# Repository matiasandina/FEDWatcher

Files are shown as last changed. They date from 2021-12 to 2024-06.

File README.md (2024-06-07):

# FEDWatcher

FEDWatcher is sofware to connect up to 4 [FED3 feeder devices](https://github.com/KravitzLabDevices/FED3/) to one Raspberry Pi 4. 
The Raspberry Pi communicates with the FED3 devices using software serial from the BNC/headphone jack port of the Adafruit feather into the activated UART channels on the Pi.

This repository contains:

* Python code that uses standard Raspberry Pi software and Python packages. 
* The modified software serial library used on the FED3 devices. See [softwareSerial](https://github.com/matiasandina/FEDWatcher/tree/main/softwareSerial).
* Files to print the PCB we are using as a Raspberry Pi HAT for easier interface with the Raspberry Pi 4 pinout. 
* Python code for FEDWatcher GUI, which provides a way for the user to create projects and trigger FEDWatcher easily (see pic below).

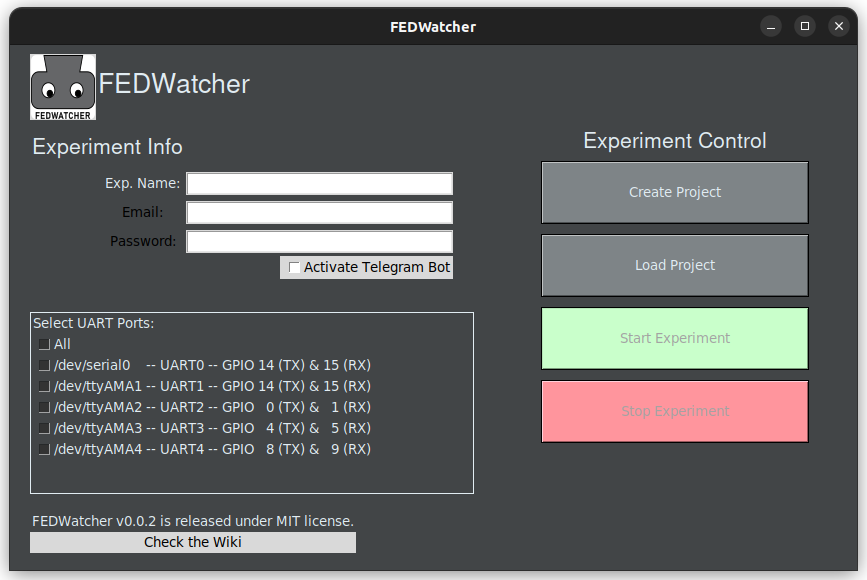
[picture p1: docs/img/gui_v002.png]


## Installation

If you already have an OS installed in your Rasberry Pi, [jump here](#edit-config). Otherwise continue reading.

To set up the Raspberry Pi, begin with flashing a standard image of Raspbian to an SD card. The project was coded and tested using Raspbian Lite with a Gnome Desktop and Raspbian Lite Buster, but any version of Raspbian should work.

For installing the operating system, the official Raspberry Pi Imager can be used. If you would like to install the Gnome desktop, the install will require that you have at least an 8GB SD card, the Pi plugged directly into a monitor, and a wifi or ethernet connection. 

### Gnome desktop

To use the Gnome desktop, first run

```
sudo raspi-config
```

Go into advanced options, select GL driver, install necessary packages if asked, and set the driver to fake KMS. Next, go back into advanced options and make sure you expand filesystem, as this is a large download. Then, back in bash, run

```
git clone https://github.com/TerraGitHuB/gnomeforpi.git && cd gnomeforpi && sudo bash gnomeforpi-install
```

This will take a long time. When the install is finished, the Raspberry Pi will reboot and you will be able to log into the Gnome desktop. In addition, the wifi will be disconnected, but you will be able to reconnect after logging in. After choosing your user and before entering your password, click the settings cog wheel under the password entry box and choose "Gnome for Xorg".

## Edit config

Next, you must enable the four hardware UARTs within the Raspberry Pi. Navigate to `/boot/` and edit `config.txt` however you prefer. This is an example using `nano`

```
sudo nano /boot/config.txt
``` 

> [!TIP]
> In newer versions, `config.txt` has been moved to `/boot/firmware/config.txt`. but everything else applies 

At the end of the file, add on the following statements:

[spi0=on]
# Settings when SPI0 is enabled: no uart4
# No need to repeat uart2, uart3, uart5 if they are always loaded

[spi0=off]
# Settings when SPI0 is disabled: include uart4
dtoverlay=uart4

[all]

dtoverlay=w1-gpio
enable_uart=1
force_eeprom_read=0
disable_poe_fan=1
dtoverlay=uart2
dtoverlay=uart3
dtoverlay=uart5

```

The first two lines disable the GPIO 0 and 1 functionality to be used for uart2. 

You can always remove/comment the first 3 lines above if you need to use a POE fan with the Pi at the same time, but it might create some unexpected erros. Please only do this if you are experienced with this type of config. 

The general mapping to. As of now, FEDWatcher only uses RX ports, but the TX pins will be reserved too.
Below there's mapping between `uartx` -> `GPIOx` -> `board pin #`

```
uart    GPIO                Board Pins (function)
--------------------------------------------------
        TXD RXD CTS RTS     
uart0   14  15              8   10
uart1   14  15              8   10
uart2   0   1   2   3       27  28  (I2C)
uart3   4   5   6   7       7   29
uart4   8   9   10  11      24  21  (SPI0)
uart5   12  13  14  15      32  33  (gpio-fan)
```

You can also check the (UART pinouts here)[https://pinout.xyz/pinout/uart].

This configuration should work when connecting FEDs directly using jumper wires or when using the HAT we designed (see further below).

> [!IMPORTANT]  
> Selecting proper pinout is key to correct functioning of the device. In general, FEDWatcher is flexible and works well with many HATs, but knowledge of the free/used pins is paramount for correct functionality.

Now, you will be able to clone the FEDWatcher github repository into your project and use the functions within it to run your own programs.

## fedwatcher python

To install the software itself, you are advised to use a virtual environment. Clone the repository and then install package requirements in the virtual environment. Installation in Raspberry Pi takes a long time, use the piwheel link in `pip3 install` to make it faster. 

Using conda:

```
git clone https://github.com/matiasandina/FEDWatcher.git
cd FEDWatcher
# tested on python 3.7.3 and 3.10
conda create -n fw_env python==3.10 pip
conda activate fw_env
pip3 install -r requirements.txt --extra-index-url https://www.piwheels.org/simple
```

Using venv (please make sure you get a python version that is compatible!): 

```
git clone https://github.com/matiasandina/FEDWatcher.git
cd FEDWatcher
python3 -m venv fedwatcher 
source fedwatcher/bin/activate
pip3 install -r requirements.txt --extra-index-url https://www.piwheels.org/simple
```

To launch the GUI.

```
cd FEDWatcher/
source fedwatcher/bin/activate
python3 fedwatcher/GUI.py
```

### Desktop entry

You can create a `FEDWatcher.desktop` file in the `Desktop` folder (e.g,. `nano /home/pi/Desktop/FEDWatcher.desktop`). The `Exec` will vary depending on how you installed FEDWatcher. Below, we reproduce an example compatible with the manual way and no virtual environment. 

```
[Desktop Entry]
Type=Application
Comment=FEDWatcher
Name=FEDWatchar
Exec=python3 /home/pi/FEDWatcher/fedwatcher/GUI.py
Icon=/home/pi/FEDWatcher/fedwatcher/img/64.png
Terminal=true
Categories=Utility
StartupNotify=true
```

---
## Hardware

FED3 needs `.ino` sketches to be flashed into it. There are a few things that are crucial for fedwatcher to work properly in FED3 devices.

### Arduino side

On the Arduino side of things, you should have a few modifications to your sketch

Use

```
#include "FED3.h"
```
This will make use of a local `FED3.h` file, instead of the installed FED3 library. We are currently trying to work out a way to merge FEDWatcher into the common FED3 library but for the time being you will need to use a local file.

Use `setSerial(true)` to enable FEDWatcher.

```
void setup() {
  fed3.begin();                                         //Setup the FED3 hardware
  fed3.DisplayPokes = false;                            //Customize the DisplayPokes option to 'false' to not display the poke indicators
  fed3.timeout = 3; //Set a timeout period (in seconds) after each pellet is taken
  
  // Turn to true if you are using FEDWatcher
  fed3.setSerial(true);
}
```

You can check the `sampleSketch` folder which has a free feeding example with 3 second inter trial interval (time between pellets).

### Pinout

To connect the FED3 devices to the Raspberry Pi, you will need a cable that takes the BNC female from the FED3 (old version) or a 3.5 mm male jack to fit the 3.5 mm female jack (new version) and ends to interface with the Raspberry Pi (see below). 

We have made custom cable using awg22 cable, BNC adapters, and male 3.5 mm jacks (see links below). If you are using the newer version of the FED3, any commercial stereo cable will work just fine.

For this program, up to four FED3 devices can be hooked up to a single Raspberry Pi. There are four activated UART ports with receivers at GPIO pins 1, 5, 9, and 13, corresponding to port1, port2, port3, port 4, in order. The unused send pins are located at 0, 4, 8, and 12. **These pins cannot be used while this program is running**. However, if not all ports are used, they can be disabled in the setup function. 

For this setup, the red/hot wire will go to one of the receiver post listed above, and the black/ground wire will go to any ground pin on the Raspberry Pi.

For more information on the pinout of the Raspberry pi visit the [Official Raspberry Documentation](https://www.raspberrypi.org/documentation/usage/gpio/). See below the official pinout for the Raspberry from the docs.

![image](https://user-images.githubusercontent.com/7494967/124830013-53691600-df47-11eb-8e53-1c78fbac09ee.png)

### Design of FEDWatcher HAT

We have also designed a little PCB board that sits on top of the RPi, so that it is easier for users to get started. This board was designed using KiCad 5.1 and 
relies on the following libraries (for footprints and parts):
- https://componentsearchengine.com/part-view/RASPBERRY%20PI%204B%20%2B%20Samtec%20ESP-120-33-G-D/RASPBERRY-PI

Here's how the PCB looks like

![FEDWatcher PCB](https://github.com/matiasandina/FEDWatcher/blob/main/hardware/RPi_shield/RPi_shield.png?raw=true)

There's a bit of soldering involved, but it makes things cleaner:

* Solder female pins to PCB to match Raspberry Pi's pinout.
* Solder female headphone jacks to PCB
* Solder male pins to match fan female connectors

These is how it looks like in our lab.

![fedwatcher-top](https://github.com/matiasandina/FEDWatcher/blob/main/docs/img/fedwatcher-top.jpg?raw=true) 
![fedwatcher-side](https://github.com/matiasandina/FEDWatcher/blob/main/docs/img/fedwatcher-side.jpg?raw=true)

The designs live on the [hardware](https://github.com/matiasandina/FEDWatcher/tree/main/hardware/RPi_shield) folder in this repository, where you can also find the bill of materials for the HAT.
There are a few generic parts that we recommend using, but similar parts should work.

* [Heat Sink and Fan](https://www.amazon.com/GeeekPi-Raspberry-Cooling-Aluminum-Heatsink/dp/B07PCMTZHF/ref=sr_1_3?crid=Q8C55QA09LS2&keywords=raspberry+pi+fan+aluminum+heatsink&qid=1659374343&sprefix=raspberry+pi+fan+aluminum+heatsink%2Caps%2C65&sr=8-3)
* [BNC adapter](https://www.amazon.com/Connector-Coaxial-Terminal-Adpater-Surveillance/dp/B091Z1V55J/ref=sr_1_22_sspa?crid=16I3NQ8L51GTH&keywords=bnc+adapter+wire&qid=1659374513&sprefix=bnc+adapters+wire,aps,61&sr=8-22-spons&psc=1)
* [M2.5 brass standoff](https://www.amazon.com/HanTof-Raspberry-Standoffs-Standoff-Cylinder/dp/B07KM27KC6/ref=pd_sbs_5/136-6686908-1264224?pd_rd_w=xld4t&pf_rd_p=0f56f70f-21e6-4d11-bb4a-bcdb928a3c5a&pf_rd_r=T61GBPY4VQAJ1AG9K1SB&pd_rd_r=d5b09aac-2d40-4798-8f3f-64e0f1895e47&pd_rd_wg=2Fxwf&pd_rd_i=B07KM27KC6&psc=1)

## Contribute

This is a primary release, please file [issues](https://github.com/matiasandina/FEDWatcher/issues) to contribute to this project.

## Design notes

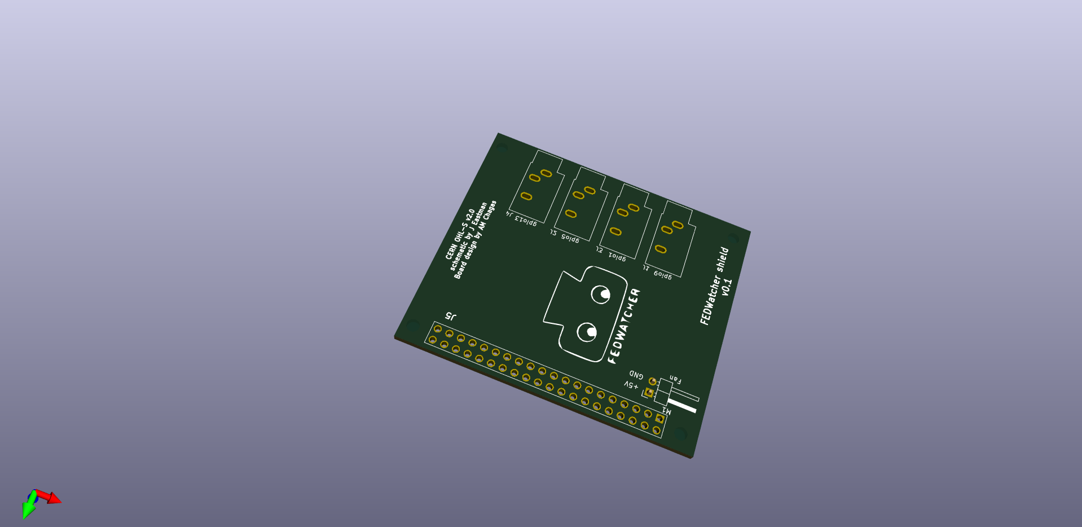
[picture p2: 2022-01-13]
hardware/RPi_shield/RPi_shield.png

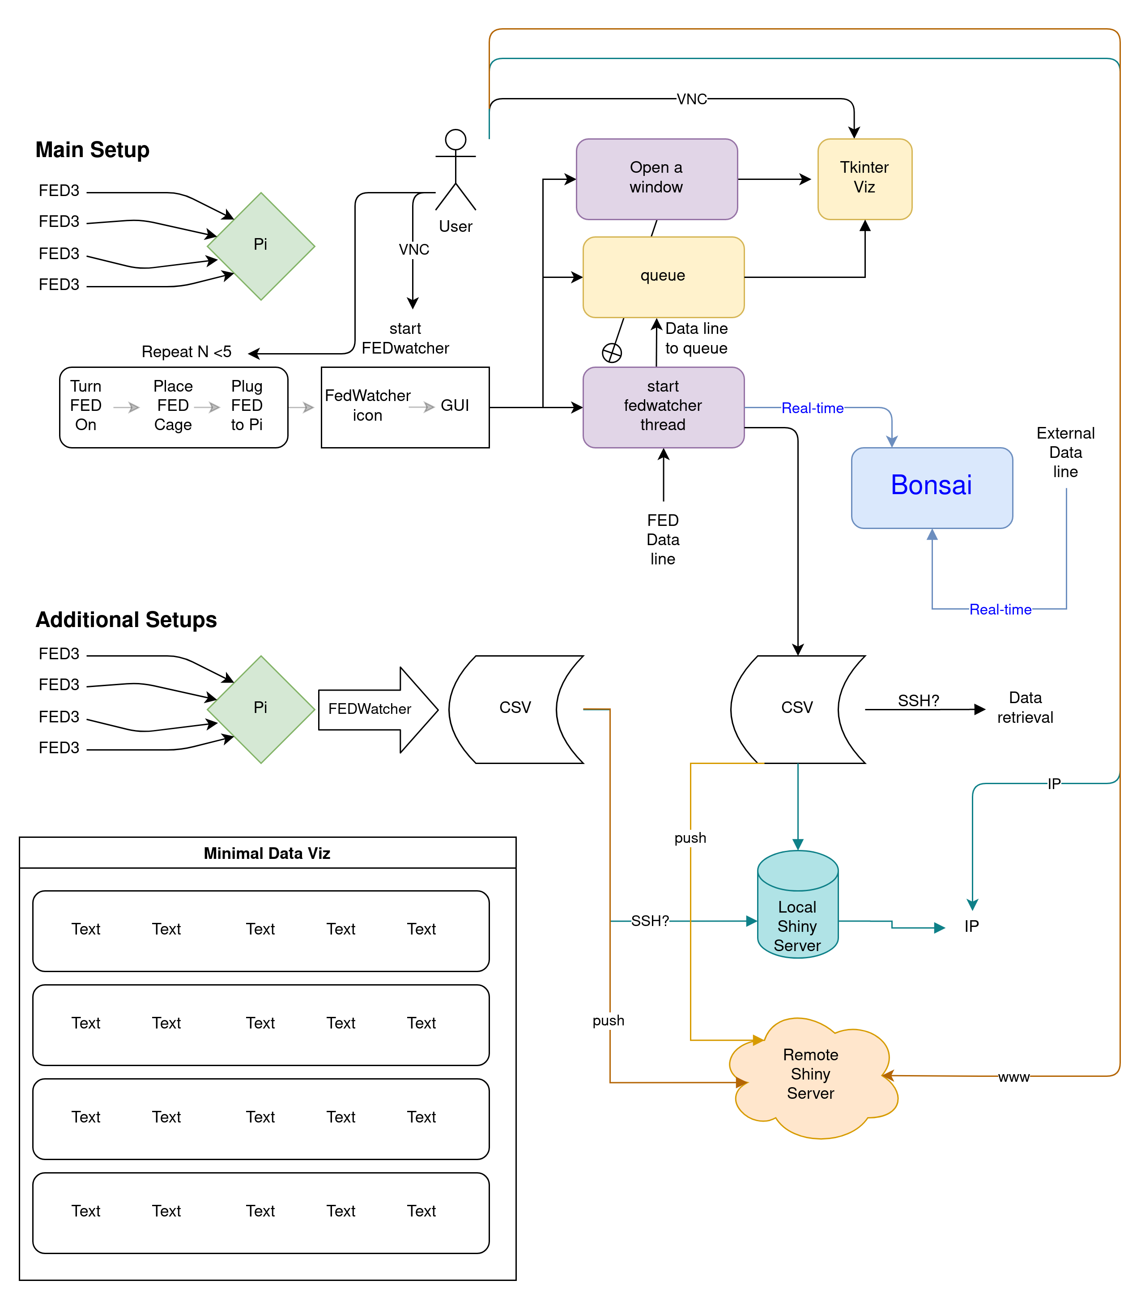
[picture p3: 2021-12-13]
docs/img/FEDWatcher.png

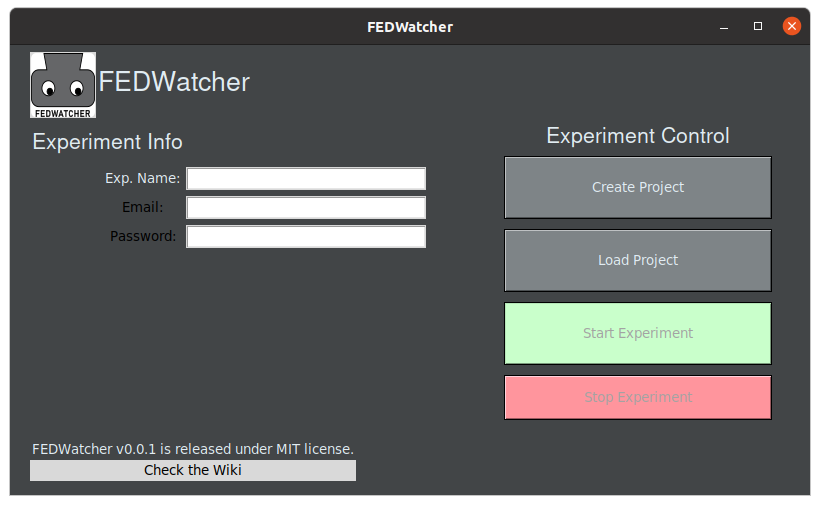
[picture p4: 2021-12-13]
docs/img/gui_v001.png

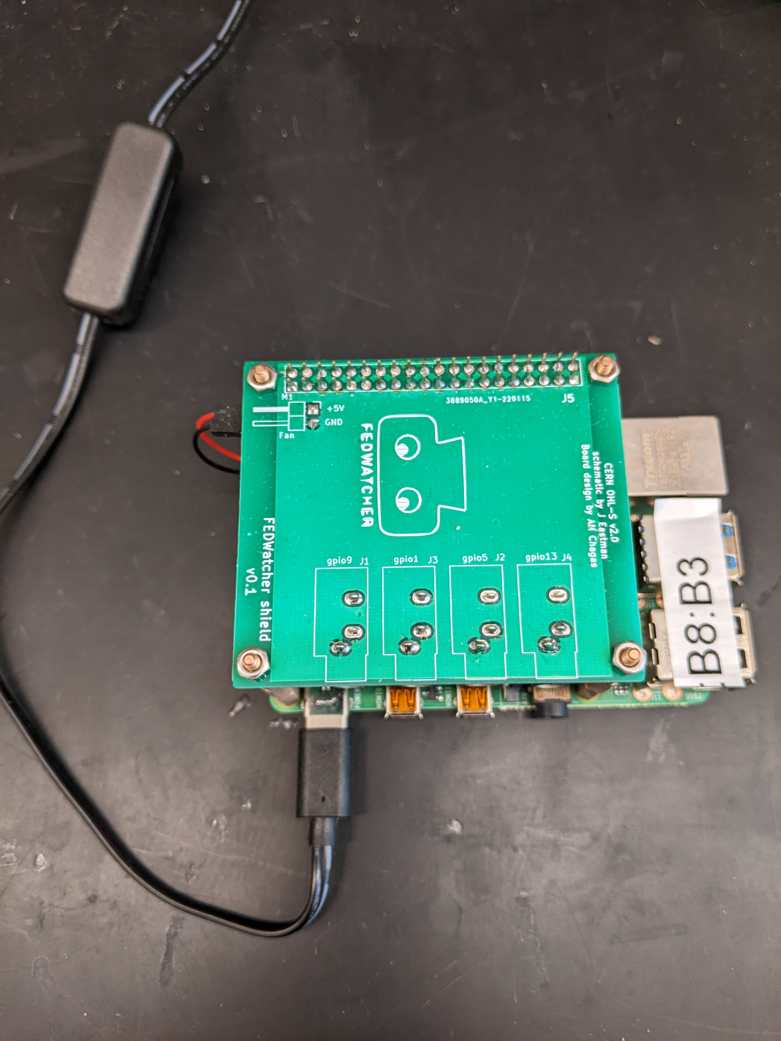
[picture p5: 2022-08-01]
docs/img/fedwatcher-top.jpg

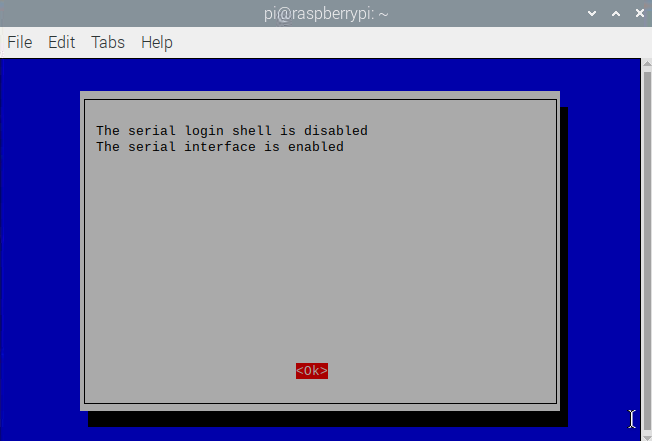
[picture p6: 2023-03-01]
docs/img/uart0_config_05.png

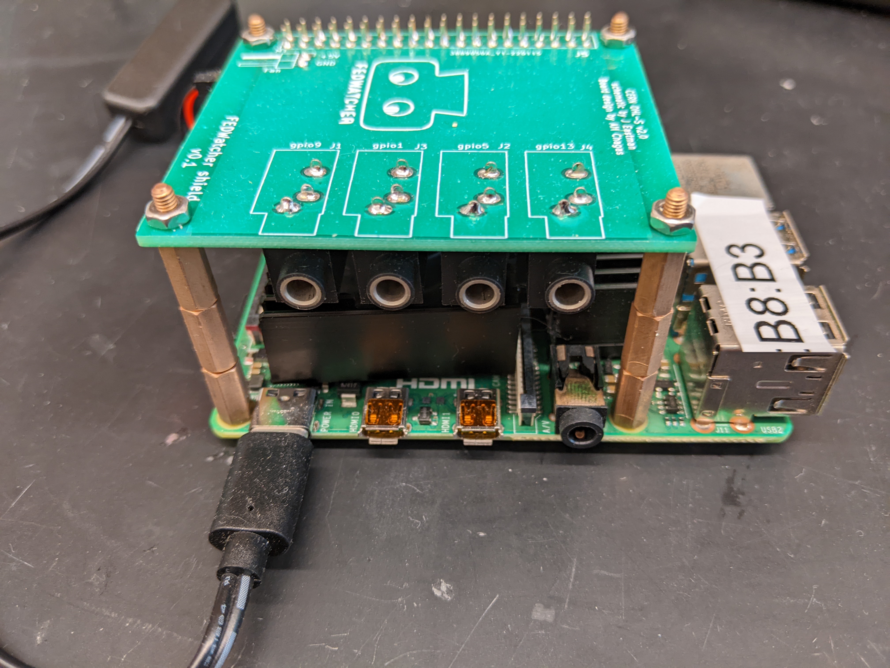
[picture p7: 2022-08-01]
docs/img/fedwatcher-side.jpg

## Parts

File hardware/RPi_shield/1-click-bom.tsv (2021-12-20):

References | Quantity | description | manufacturer | mpn | mouser
J1,J2,J3,J4 | 4 | Audio Jack 3.5mm 3 pins | CUI | SJ1-3533NG | 490-SJ1-3533NG
J5 | 1 | RASPBERRY_PI_4B_+_Samtec_ | Samtec | ESQ-120-33-G-D | 200-ESQ12033GD
M1 | 1 | Fan connector PinHeader_1x02_P2.54mm | Harwin | M20-9750242 | 855-M20-9750242

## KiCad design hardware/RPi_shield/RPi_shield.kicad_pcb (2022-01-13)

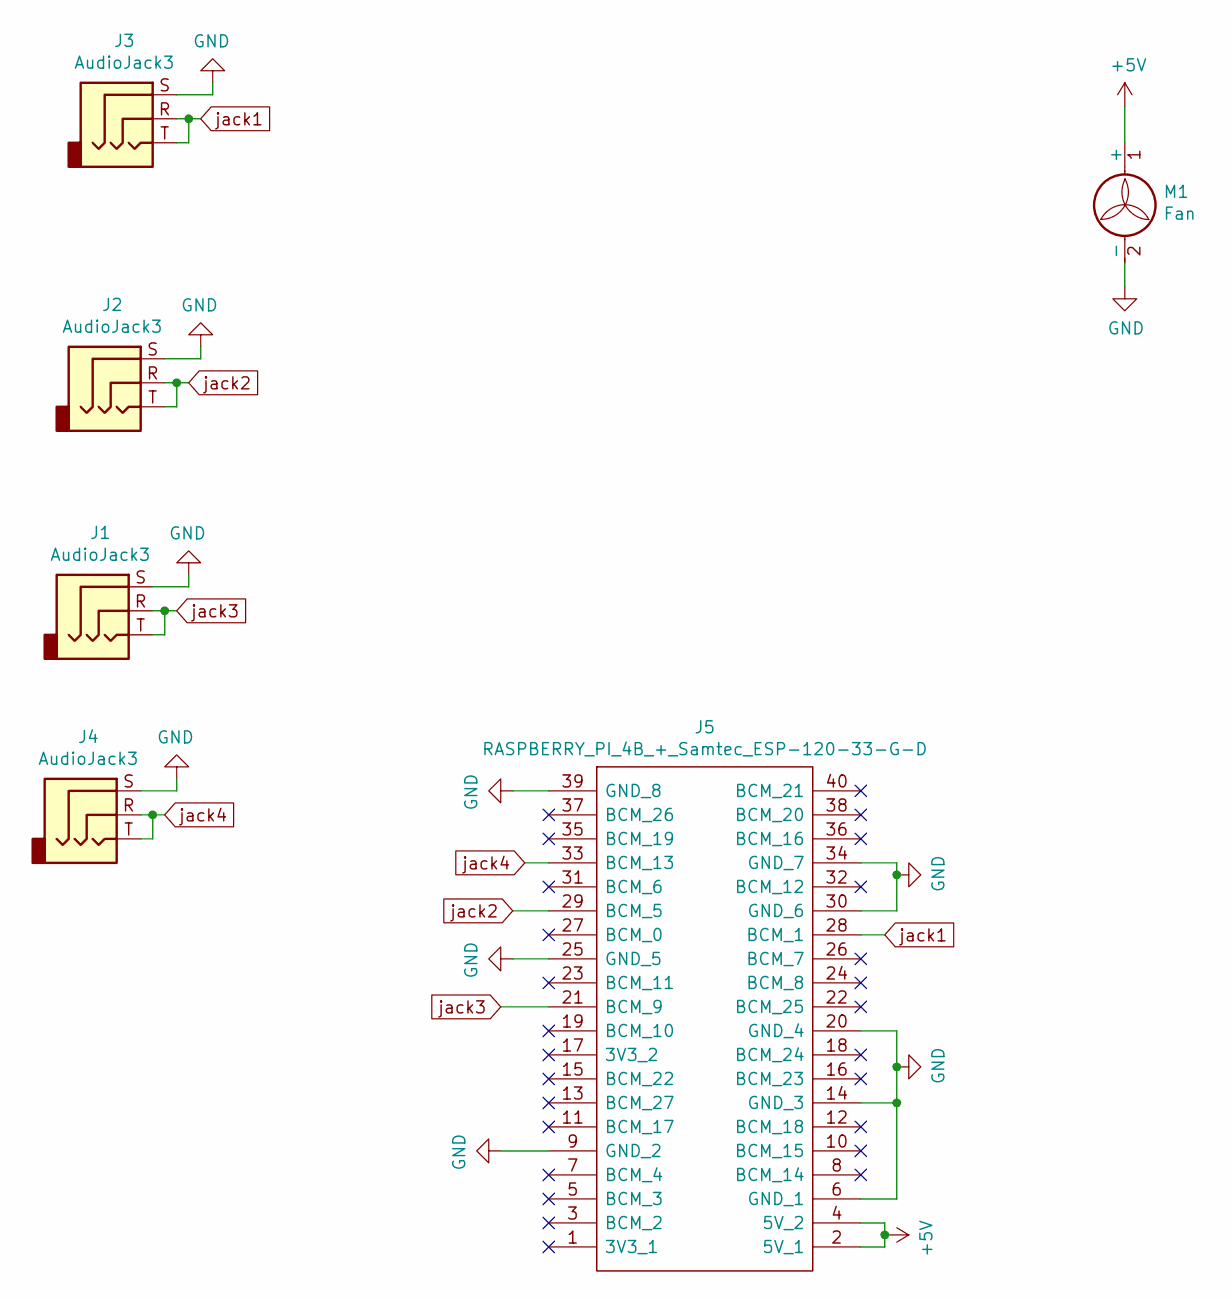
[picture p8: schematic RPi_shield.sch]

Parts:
J1, J2, J3, J4: AudioJack3; Jack_3.5mm_CUI_SJ1-3533NG_Horizontal
J5: RASPBERRY_PI_4B_+_Samtec_ESP-120-33-G-D; RASPBERRYPI4B4GB; Manufacturer_Part_Number RASPBERRY PI 4B + Samtec ESP-120-33-G-D
M1: Fan; PinHeader_1x02_P2.54mm_Horizontal

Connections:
+5V: J5.2 (5V_1), J5.4 (5V_2), M1.1 (+)
GND: J1.S, J2.S, J3.S, J4.S, J5.6 (GND_1), J5.9 (GND_2), J5.14 (GND_3), J5.20 (GND_4), J5.25 (GND_5), J5.30 (GND_6), J5.34 (GND_7), J5.39 (GND_8), M1.2 (-)
jack1: J3.R, J3.T, J5.28 (BCM_1)
jack2: J2.R, J2.T, J5.29 (BCM_5)
jack3: J1.R, J1.T, J5.21 (BCM_9)
jack4: J4.R, J4.T, J5.33 (BCM_13)

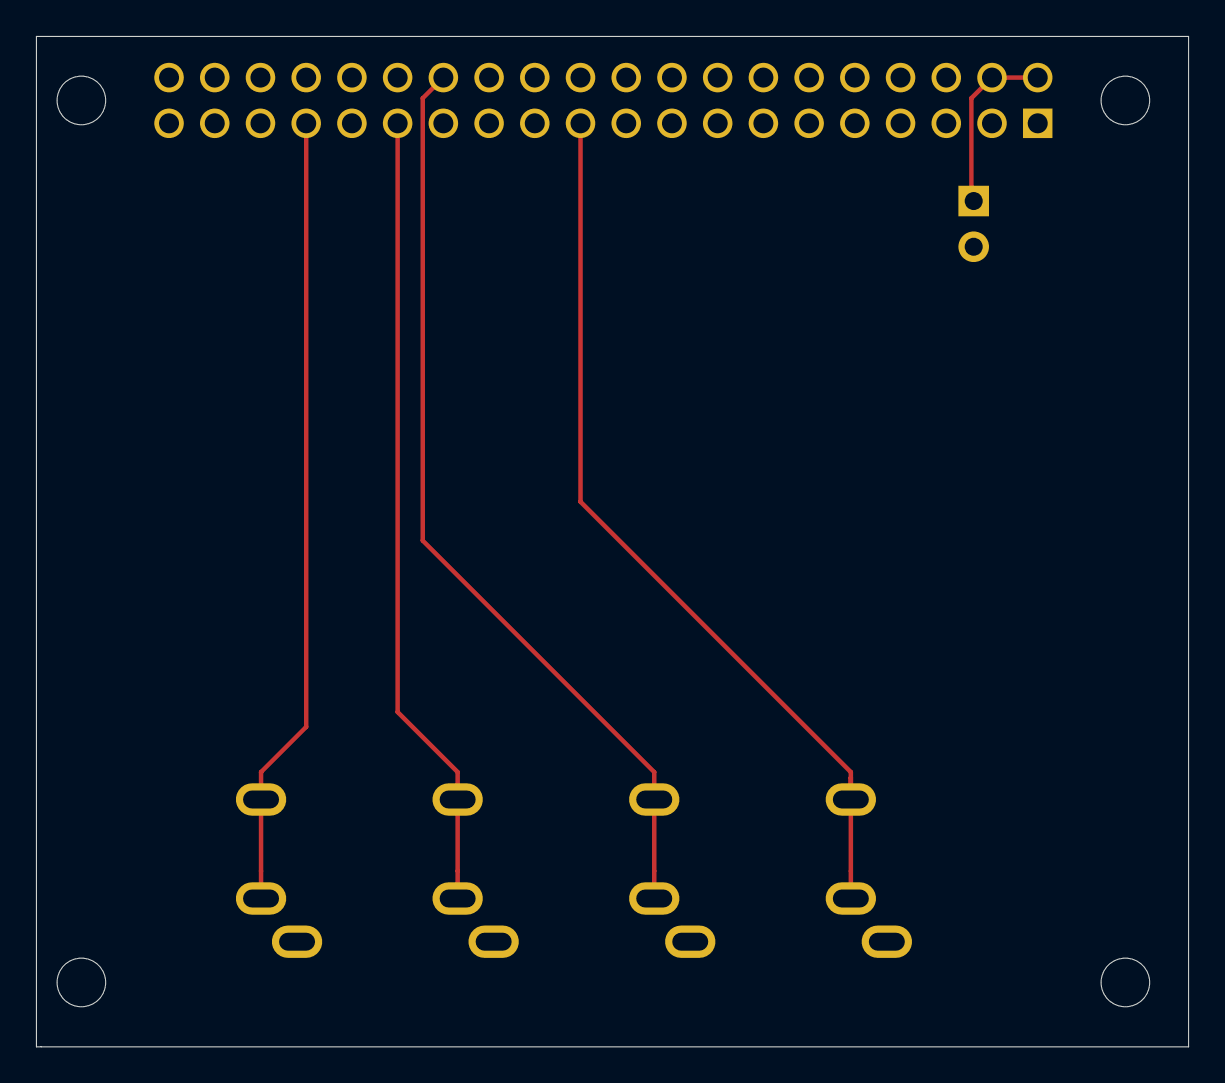
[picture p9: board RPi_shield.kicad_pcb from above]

Board: 2 copper layers, 64.0 x 56.1 mm, 6 parts (0 on the bottom side), 6 nets.

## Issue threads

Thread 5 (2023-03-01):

### ISSUE TITLE
Detecting jams & Notifying People

### ISSUE THREAD

**Issue by matiasandina** [matiasandina/FEDWatcher#5]
- [x] On `FED_library` we want to set a timer that lets us know through serial if clearing jam is not solved within 10 min. Send "special alert"
- [X] On `FEDWatcher` we should be watching for jams. So parse `Device_Number`, "jam"
- [x] Alert user via email

**Comment by matiasandina** [comment]
I want to reopen this.
We didn't have the best of experience with setting up emails and stuff...there might be a workaround by using something like twillio (or any other app) + python authomation + whatsapp

See [here](https://www.twilio.com/docs/whatsapp/tutorial/send-and-receive-media-messages-whatsapp-python)

**Comment by matiasandina** [comment]
We can send messages with something like this (given we have `secrets.py`) and have done the telegram configuration. 
We would need to integrate the proper messaging with parsing data for each FED and/or jamming events and send proper messaging.

Brainstorm of what would be nice to have:

* FED00X is jammed
* FED00X delivered Y number of pellets in the last n hours

```
import requests
from secrets import secrets
import seaborn as sns
# Send a telegram message to a given user id
def send_message (chatId, message):
    response = requests.post(sendURL + "?chat_id=" + str(chatId) + "&text=" + message)
    # Close to avoid filling up the RAM.
    response.close()

if __name__ == '__main__':
    botToken = secrets['botToken']
    chatId = secrets['telegramDmUid']

    # Telegram send message URL
    sendURL = 'https://api.telegram.org/bot' + botToken + '/sendMessage'
    
    iris = sns.load_dataset('iris')
    message =  str(iris.head())

    send_message(chatId, message)
```

**Comment by cameron4young** [comment]
Here's what I've coded for the runHelper and event_summary functions:

Lines 235-247 (runHelper)
```
            # TODO: replicate this idea but with the notification interval
            if (now - self.last_notif * 3600) > self.notif_interval:
                self._save_all_df()
                # create read_csv_
                self.last_save = now
                current_directory = os.getcwd() # gets path to current folder (src)
                data_folder_path = os.path.join(current_directory, 'data') # gets the path to the data folder
                csv_files = [file for file in os.listdir(data_folder_path) if file.endswith('.csv')]
                for path in csv_files:
                    summary = self.event_summary(path)
                    if self.tg_enabled:
                        self.send_tg_message(message=summary)
                self.last_notif = now # updates last_notif to the current time
```

Event summary
```
def event_summary(self, path):
    ## want to return message in format "FED{Device #} delivered {num_rows} pellets since {Time}"
    # INPUTS: data, last time interval
    # OUTPUTS: a summarized message in string form

    # iterate through dataframe
    df = pd.read_csv(path)
    device_number = path.split("_")[0]
    # filter through events using PiTime
    filtered_df = df.loc[df['Pi_Time'] > self.last_notif & (df['Pi_Time'] < self.now) & (df['Event']=="Pellet")]
    # pellets = number of rows in df after filtering
    num_pellets = len(filtered_df.index) # will this work with empty df?
    return f"FED{device_number} delivered {num_pellets} since {self.last_notif}"

```

The function accesses the 'data' folder by using the os.path.join function. A list of paths to all of the csv files are then created. This list is iterated upon, with each file being read and turned into a pandas dataframe within the event_summary function. After the conversion to a pandas dataframe, the dataframe is filtered to only show the data we are interested in, and a summary message is then created and sent. After all of this happens, we then set the last_notif variable to now, and the process repeats every notif_interval.

**Comment by matiasandina** [comment]
As is, this will not run. Here are a few of issues I modified.

* `now = time.time()` (also used for `self.last_save`) cannot be used to filter a `dataframe` with a `datetime` column
* `self.now` does not exist, created a `self.now_dt` to make it different from the `time.time()` version of it which is stored at `now`
`path_split` will not work as expected when using a full path (which we need for reading!)

These lines are searching for data where the data is *not* being saved

```
              current_directory = os.getcwd() # gets path to current folder (src)
                data_folder_path = os.path.join(current_directory, 'data') # gets the path to the data folder
 
```

Data gets saved in 

```
self.exp_dir 
```
and split by day into

```
self.today_dir
```

**Comment by matiasandina** [comment]
Also, this line turned out to be wrong
```
filtered_df = df.loc[df['Pi_Time'] > self.last_notif & (df['Pi_Time'] < self.now_dt) & (df['Event']=="Pellet")]
TypeError: Cannot perform 'rand_' with a dtyped [bool] array and scalar of type [bool]

```

The issue were missing parenthesis on the first condition

***

More importantly this code didn't reset the last_notif and therefore it was blasting notifications one after the other on each iteration. It was missing

```
self.last_notif = self.now_dt
```

**Comment by matiasandina** [comment]
Looks like mvp is working. Closing until further enhancement is needed. 
![image](https://user-images.githubusercontent.com/7494967/222281846-ecfba089-affc-4b9c-a76b-091f5f62bd96.png)

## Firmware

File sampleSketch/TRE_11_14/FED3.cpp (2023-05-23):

/*
  Feeding experimentation device 3 (FED3) library
  Code by Lex Kravitz, adapted to Arduino library format by Eric Lin
  alexxai@wustl.edu
  erclin@ucdavis.edu
  December 2020 

  The first FED device was developed by Nguyen at al and published in 2016:
  https://www.ncbi.nlm.nih.gov/pubmed/27060385

  FED3 includes hardware and code from:
  *** Adafruit, who made the hardware breakout boards and associated code we used in FED ***

  Cavemoa's excellent examples of datalogging with the Adalogger:
  https://github.com/cavemoa/Feather-M0-Adalogger

  Arduino Time library http://playground.arduino.cc/code/time
  Maintained by Paul Stoffregen https://github.com/PaulStoffregen/Time

  This project is released under the terms of the Creative Commons - Attribution - ShareAlike 3.0 license:
  human readable: https://creativecommons.org/licenses/by-sa/3.0/
  legal wording: https://creativecommons.org/licenses/by-sa/3.0/legalcode
  Copyright (c) 2019, 2020 Lex Kravitz
*/


/**************************************************************************************************************************************************
                                                                                                    Startup stuff
**************************************************************************************************************************************************/
#include "Arduino.h"
#include "FED3.h"

//  Start FED3 and RTC objects
FED3 *pointerToFED3;
RTC_PCF8523 rtc; 

//  Interrupt handlers
static void outsidePelletTriggerHandler(void) {
  pointerToFED3->pelletTrigger();
}

static void outsideLeftTriggerHandler(void) {
  pointerToFED3->leftTrigger();
}

static void outsideRightTriggerHandler(void) {
  pointerToFED3->rightTrigger();
}

/**************************************************************************************************************************************************
                                                                                                        Main loop
**************************************************************************************************************************************************/
void FED3::run() {
  //This should be called at least once per loop.  It updates the time, updates display, and controls sleep 
  if (digitalRead(PELLET_WELL) == HIGH) {  //check for pellet
    PelletAvailable = false;
  }
  DateTime now = rtc.now();
  currentHour = now.hour(); //useful for timed feeding sessions
  unixtime  = now.unixtime();
  ReadBatteryLevel();
  UpdateDisplay();
  goToSleep();
}

/**************************************************************************************************************************************************
                                                                                                Poke functions
**************************************************************************************************************************************************/
//log left poke
void FED3::logLeftPoke(){
  if (PelletAvailable == false){
    leftPokeTime = millis();
    LeftCount ++;
    leftInterval = 0.0;
    while (digitalRead (LEFT_POKE) == LOW) {}  //Hang here until poke is clear
    leftInterval = (millis()-leftPokeTime);
    if (leftInterval < minPokeTime) {
      Event = "LeftShort";
    }
    else{
      Event = "Left";
    }
    logdata();
    UpdateDisplay();
    DisplayLeftInt();
    Left = false;
  }
}

//log right poke
void FED3::logRightPoke(){
  if (PelletAvailable == false){
    rightPokeTime = millis();
    RightCount ++;
    rightInterval = 0.0;
    while (digitalRead (RIGHT_POKE) == LOW) {} //Hang here until poke is clear
    rightInterval = (millis()-rightPokeTime);
    if (rightInterval < minPokeTime) {
      Event = "RightShort";
    }
    else{
      Event = "Right";
    }
    logdata();
    UpdateDisplay();
    DisplayRightInt();
    Right = false; 
  }
}

void FED3::randomizeActivePoke(int max){
  //Store last active side and randomize
  byte lastActive = activePoke;
  activePoke = random (0, 2);
  Serial.print("ActivePoke: ");
  Serial.println(activePoke);

  //Increment consecutive active pokes, or reset consecutive to zero
  if (activePoke == lastActive) {
    consecutive ++;
  }
  else {
    consecutive = 0;
  }
  
  //if consecutive pokes are too many, swap pokes
  if (consecutive >= max){
    Serial.println("SWAPPING");
    if (activePoke == 0) {
      activePoke = 1;
    }
    else if (activePoke == 1) {
      activePoke = 0;
    }
    consecutive = 0;
    Serial.print("New ActivePoke: ");
    Serial.println(activePoke);
    }
  Serial.println();
}

/**************************************************************************************************************************************************
                                                                                                Feeding functions
**************************************************************************************************************************************************/
void FED3::Feed() {
  //Run this loop repeatedly until statement below is false
  bool pelletDispensed = false;
  
  do {	
	
    if (pelletDispensed == false) {
	    pelletDispensed = RotateDisk(-300);
    }

    pixelsOff();

    //If pellet is detected during or after this motion
    if (pelletDispensed == true) {
      digitalWrite (MOTOR_ENABLE, LOW);  //Disable motor driver and neopixel
      pelletTime = millis();
      
      display.fillCircle(25, 99, 5, BLACK);
      display.refresh();
      retInterval = (millis() - pelletTime);
      //while pellet is present and under 60s has elapsed
      while (digitalRead (PELLET_WELL) == LOW and retInterval < 60000) {  //After pellet is detected, hang here for up to 1 minute to detect when it is removed
        retInterval = (millis() - pelletTime);
        DisplayRetrievalInt();
       
        //Log pokes while pellet is present 
        if (digitalRead(LEFT_POKE) == LOW) {             //If left poke is triggered
          leftPokeTime = millis();
          LeftCount ++;
          leftInterval = 0.0;
          while (digitalRead (LEFT_POKE) == LOW) {}  //Hang here until poke is clear
          leftInterval = (millis()-leftPokeTime);
          UpdateDisplay();
          Event = "LeftWithPellet";
          logdata();
          }

        if (digitalRead(RIGHT_POKE) == LOW) {            //If right poke is triggered
          rightPokeTime = millis();
          RightCount ++;
           rightInterval = 0.0;
          while (digitalRead (RIGHT_POKE) == LOW) {}  //Hang here until poke is clear
          rightInterval = (millis()-rightPokeTime);
          UpdateDisplay();
          Event = "RightWithPellet";
          logdata();       
          }
        } 
      
      //after 60s has elapsed
      while (digitalRead (PELLET_WELL) == LOW) { //if pellet is not taken after 60 seconds, wait here and go to sleep
        run();
        //Log pokes while pellet is present 
        if (digitalRead(LEFT_POKE) == LOW) {             //If left poke is triggered
          leftPokeTime = millis();
          LeftCount ++;
          leftInterval = 0.0;
          while (digitalRead (LEFT_POKE) == LOW) {}  //Hang here until poke is clear
          leftInterval = (millis()-leftPokeTime);
          UpdateDisplay();
          Event = "LeftWithPellet";
          logdata();
          }

        if (digitalRead(RIGHT_POKE) == LOW) {            //If right poke is triggered
          rightPokeTime = millis();
          RightCount ++;
           rightInterval = 0.0;
          while (digitalRead (RIGHT_POKE) == LOW) {}  //Hang here until poke is clear
          rightInterval = (millis()-rightPokeTime);
          UpdateDisplay();
          Event = "RightWithPellet";
          logdata();       
          }
      }

      digitalWrite (MOTOR_ENABLE, LOW);  //Disable motor driver and neopixel
      PelletCount++;
      Left = false;
      Right = false;
      Event = "Pellet";
      
      //calcualte IntetPelletInterval
      DateTime now = rtc.now();
      interPelletInterval = now.unixtime() - lastPellet;  //calculate time in seconds since last pellet logged
      lastPellet  = now.unixtime();
     
      logdata();
      numMotorTurns = 0; //reset numMotorTurns
      PelletAvailable = true;
      UpdateDisplay();
      if (timeout > 0) Timeout(timeout); //timeout after each pellet is dropped (you can edit this number)
      break;
    }

    if (PelletAvailable == false){
        pelletDispensed = dispenseTimer_ms(1500);  //delay between pellets that also checks pellet well
        numMotorTurns++;

        //Jam clearing movements
		if (pelletDispensed == false) {
          if (numMotorTurns % 5 == 0) {
            pelletDispensed = MinorJam();
          }
		}
        if (pelletDispensed == false) {
          if (numMotorTurns % 10 == 0 and numMotorTurns % 20 != 0) {
            pelletDispensed = VibrateJam();
          }
		}
        if (pelletDispensed == false) {
          if (numMotorTurns % 20 == 0) {
            pelletDispensed = ClearJam();
          }
		}
    }
  } while (PelletAvailable == false);
}

//minor movement to clear jam
bool FED3::MinorJam(){
	return RotateDisk(100);
}
	
//vibration movement to clear jam
bool FED3::VibrateJam() {
    DisplayJamClear();
	
	//simple debounce to ensure pellet is out for at least 250ms
	if (dispenseTimer_ms(250)) {
	  display.fillRect (5, 15, 120, 15, WHITE);  //erase the "Jam clear" text without clearing the entire screen by pasting a white box over it
	  return true;
	}	
	for (int i = 0; i < 30; i++) {
	  if (RotateDisk(120)) {
	    display.fillRect (5, 15, 120, 15, WHITE);  //erase the "Jam clear" text without clearing the entire screen by pasting a white box over it
	    return true;
	  }
	  if (RotateDisk(-60)) {
	    display.fillRect (5, 15, 120, 15, WHITE);  //erase the "Jam clear" text without clearing the entire screen by pasting a white box over it
	    return true;
	  }
	}
	return false;
}

//full rotation to clear jam
bool FED3::ClearJam() {
    DisplayJamClear();
    if (serialOn) {
      jamAlertUpdate();
    }
	
	if (dispenseTimer_ms(250)) {
	  display.fillRect (5, 15, 120, 15, WHITE);  //erase the "Jam clear" text without clearing the entire screen by pasting a white box over it
	  return true;
	}
	
	for (int i = 0; i < 21 + random(0, 20); i++) {
	  if (RotateDisk(-i * 4)) {
	    display.fillRect (5, 15, 120, 15, WHITE);  //erase the "Jam clear" text without clearing the entire screen by pasting a white box over it
	    return true;
	  }
	}
	
	if (dispenseTimer_ms(250)) {
	  display.fillRect (5, 15, 120, 15, WHITE);  //erase the "Jam clear" text without clearing the entire screen by pasting a white box over it
	  return true;
	}
	
	for (int i = 0; i < 21 + random(0, 20); i++) {
	  if (RotateDisk(i * 4)) {
	    display.fillRect (5, 15, 120, 15, WHITE);  //erase the "Jam clear" text without clearing the entire screen by pasting a white box over it
	    return true;
	  }
	}
	
	return false;
}

bool FED3::RotateDisk(int steps) {
  digitalWrite (MOTOR_ENABLE, HIGH);  //Enable motor driver
  for (int i = 0; i < (steps>0?steps:-steps); i++) {	  
	  if (steps > 0)
		  stepper.step(1);
	  else
		  stepper.step(-1);	  
	  for (int j = 0; j < 20; j++){
		delayMicroseconds(100);		
		if (digitalRead (PELLET_WELL) == LOW) {
		  delayMicroseconds(100);
		  // Debounce
		  if (digitalRead (PELLET_WELL) == LOW) {
		    ReleaseMotor ();
		    return true;
		  }
		}
	  }
    }
	ReleaseMotor ();
	return false;
}

//Function for delaying between motor movements, but also ending this delay if a pellet is detected
bool FED3::dispenseTimer_ms(int ms) {
  for (int i = 1; i < ms; i++) {
    for (int j = 0; j < 10; j++) {
  	  delayMicroseconds(100);		
	  if (digitalRead (PELLET_WELL) == LOW) {
		delayMicroseconds(100);
		// Debounce
		if (digitalRead (PELLET_WELL) == LOW) {
		  return true;
		}
	  }
	}
  }
  return false;
}
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

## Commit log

2021-07-12 adding sample data for troubleshooting dashboard
    [FED006_031721_04.CSV, FED007_031821_00.CSV, FED010_031721_00.CSV, FED011_031821_00.CSV]
2021-08-11 implemented exp_end datetime, added new sample data
    [FED17_081021_00.csv, FED17_081021_01.csv]
2021-12-13 forgot 5v connection
2021-12-17 initial pcb implementation
    [RPi_shield.kicad_pcb, RPi_shield.sch]
2021-12-17 save and push work
    [RPi_shield.sch]
2021-12-20 adding camera scriptswithout f(x) yet
2021-12-20 finish first iteration of the board and prepare it for kitspace
    [1-click-bom.tsv, RPi_shield-B_Adhes.gbr, RPi_shield-B_CrtYd.gbr, RPi_shield-B_Cu.gbr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]
2021-12-20 add last saves to kicad
    [RPi_shield.kicad_pcb, RPi_shield.sch]
2022-01-13 reverse labeling and add logo
    [RPi_shield-B_Adhes.gbr, RPi_shield-B_CrtYd.gbr, RPi_shield-B_Cu.gbr, RPi_shield-B_Fab.gbr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]
2022-01-13 save latest board state
    [RPi_shield.kicad_pcb]
2023-03-02 improving Tg and adding battery info #19
2024-06-05 imporving prints

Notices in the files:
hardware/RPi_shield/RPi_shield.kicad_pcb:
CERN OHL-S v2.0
